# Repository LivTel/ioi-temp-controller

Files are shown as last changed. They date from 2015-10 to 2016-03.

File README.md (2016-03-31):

ioi-temp-controller
=============

# Overview

This package contains the electronic schematics and arduino code to drive a 
10 microamp excitation current required by the DT-400 series temperature 
sensor diodes inside IO:I's cryostat. This facility was originally provided 
by the Lakeshore 331 temperature controller. 

# Commands

The mac, ip, gateway and subnet addresses need to be configured first.

On upload to an ethernet arduino, a socket server is instantiated to serve a limited command set previously 
used by IO:I's ICS. The four commands that are currently available are:

| Command        | Description                        |
| :------------- | :----------------                  | 
| KRDG?A         | Read temperature from sensor A (K) |
| KRDG?B         | Read temperature from sensor B (K) |
| VRDG?A         | Read voltage from sensor A (V)     |
| VRDG?B         | Read voltage from sensor B (V)     |

The socket server is blocking, and must not be held open for prolonged periods by a single machine.

## Schematic

The schematic is as follows.

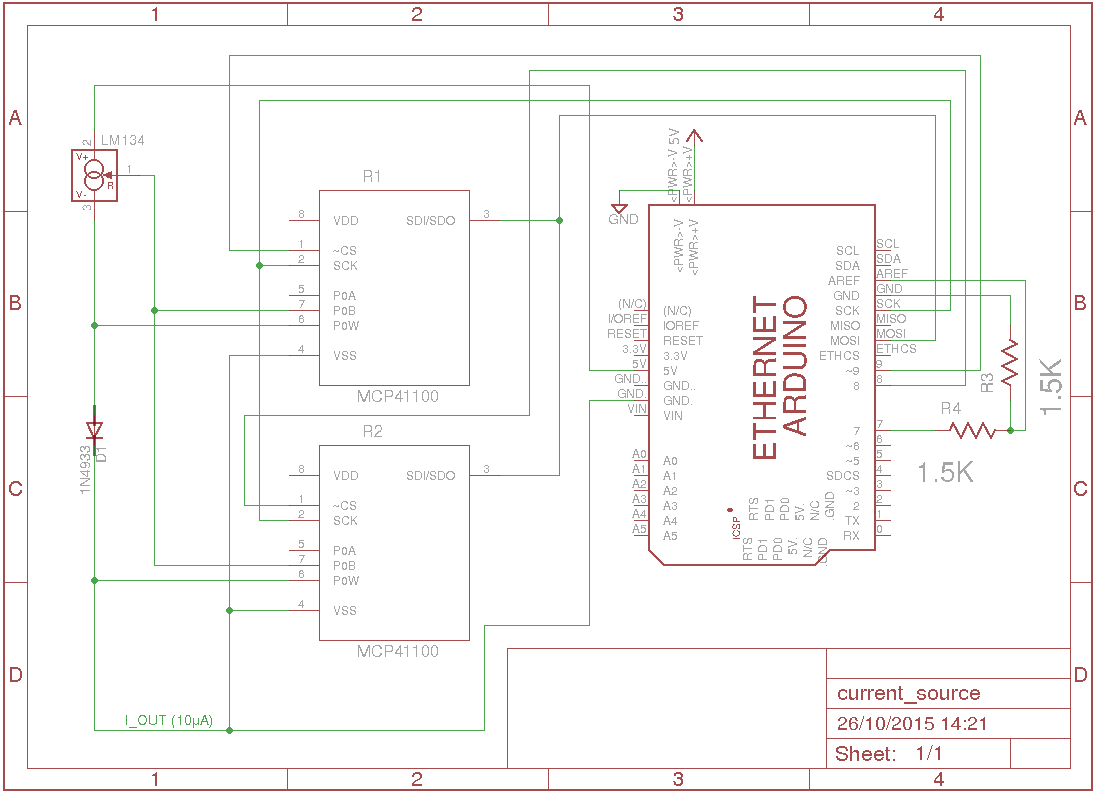
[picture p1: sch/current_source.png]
Schematic

 
The LM134 IC provides a temperature dependent current source. The magnitude of this 
current source is modulated by the two digital pots R1 & R2 (MCP41100). The 
temperature dependence is largely removed by diode D1 (1N4933). 

Note that the ETHCS pin is not used for clock selects!

# I/O Configuration

Definitions for I/O should not need to be changed if the wiring follows the schematic above *and* the 
temperature sensor wiring follows:

| Pin            | Description       |
| :------------- | :---------------- | 
| 2              | T2 V-             |
| 3              | T2 V+             |
| 4              | T1 V-             |
| 5              | T1 V+             |

# Current Magnitude and Temperature Calibration Coefficients

The set current [**SET\_CURRENT**] must be set so that it lies within the capability defined by the relative 
resistances of the digital pots. See p8 of the LM234 component manual in `man/` for a description of how the 
current magnitude is defined using the two pots.

The temperature sensor calibration is defined by the coefficients [**DIODE\_TEMPERATURE\_COEFFS**] and 
a corresponding reference voltage [**REFERENCE\_VOLTAGE**]. This has been set (as of 19/10/15) for 
a DT471 series diode.

# Known Issues

A 2.5V reference voltage is fed to the reference pin to increase the accuracy of the A2D conversion whilst still
remaining in range of the full output voltage of the diode at RT down to 80K. Currently, with the 10bit conversion 
and a diode temperature coefficient of -2.5mV/degC, the system is only accurate to [2.5/(2^10)]/(2.5*10^-3) 
degC == 1 degC. This could be improved by either i) addition of a more accurate A2D circuit, or ii) reducing the range 
over which the sensor can be read.

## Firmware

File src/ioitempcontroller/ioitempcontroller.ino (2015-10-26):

// LM134 datasheet (http://www.ti.com/lit/ds/symlink/lm234.pdf)
// MCP41100 datasheet (http://docs-europe.electrocomponents.com/webdocs/1380/0900766b81380ca2.pdf)
// DT471 datasheet (http://www.lakeshore.com/Documents/LSTC_DT400_l.pdf)

#include <SPI.h>
#include <Ethernet.h>

// NETWORK
// -------
// ARI LOCAL NETWORK
//byte mac[]     = { 0x90, 0xA2, 0xDA, 0x0E, 0x50, 0x9E };
//byte ip[]      = { 150, 204, 241, 253 }; 
//byte gateway[] = { 150, 204 ,241 ,254 };
//byte subnet[]  = { 255, 255 ,255 ,0 };

// TELESCOPE NETWORK
// ioitempcontroller
//byte mac[]     = { 0x90, 0xA2, 0xDA, 0x0E, 0x50, 0x9E };
byte mac[]     = { 0x90, 0xA2, 0xDA, 0x0D, 0xCB, 0x08 };
byte ip[]      = { 192, 168, 1, 75 };
byte gateway[] = { 192, 168 ,1 ,254 };
byte subnet[]  = { 255, 255 ,255 ,0 };

int SERVER_PORT = 8888;

// I/O
// ---
#define REF_pin 7                   // pin to pull high for voltage divided reference.
#define R1_CS_pin  9                // clock select for R1
#define R2_CS_pin  8                // clock select for R2
#define T1_ANALOG_PIN_VPLUS 5       // analog pin for T1 V+
#define T1_ANALOG_PIN_VMINUS 4      // analog pin for T1 V-
#define T2_ANALOG_PIN_VPLUS 3       // analog pin for T2 V+
#define T2_ANALOG_PIN_VMINUS 2      // analog pin for T2 V-

// CURRENT SOURCE
// --------------
// the following section works out what resistances are required to keep a particular set current
// n.b. you can't have a resistance value > the limit of the digital pots (~90K), this corresponds
// to a lower limit of ~13uA.
float SET_CURRENT             = 9*pow(10, -6);   // A
float DIODE_FORWARD_VOLTAGE   = 0.5;              // V
float DIODE_TEMPERATURE_COEFF = -2.5;             // mV/degC

// TEMPERATURE SENSOR
// ------------------
// AS OF 19/10/15, for DT471.
int DIODE_TEMPERATURE_ORDER = 5;
float DIODE_TEMPERATURE_COEFFS[6] = {-906.15255839, 3184.68704355, -4521.75268022, 3189.42006723, -1526.98411765, 668.57235871};
float REFERENCE_VOLTAGE = 2.427;

//float DIODE_FORWARD_VOLTAGE_TEMPERATURE_SENSOR   = 0.54294;  // V (DT471)
//float DIODE_TEMPERATURE_COEFF_TEMPERATURE_SENSOR = -2.0; // mV/degC (DT471)

// PROGRAM PARAMETERS
// --------------
#define NUMREADINGS     10      // number of readings to take to define average analog read
#define NUMREADINGSOMIT 10      // number of analog reads to take before taking actual reading


float get_R1_for_given_set_current(float i_set, float resistor_ratio) {
  return ((resistor_ratio*67.7*pow(10, -3)) + ((67.7*pow(10, -3)) + DIODE_FORWARD_VOLTAGE))/(resistor_ratio*i_set);  // this is taken from p9 of the lm134 datasheet
}

int digitalPotWrite(int value, int address, int pin)
{
  digitalWrite(pin, LOW);
  SPI.transfer(address);
  SPI.transfer(value);
  digitalWrite(pin, HIGH);
}

void BubbleSort(float analogValues[])
{  
  int i, j;
  for (i=0; i<NUMREADINGS; i++)
  {
    for (j=0; j<i; j++)
    {
      if (analogValues[i] > analogValues[j]) // out of order?
      {
        // swap
        float temp = analogValues[i];
        analogValues[i] = analogValues[j];
        analogValues[j] = temp;
      }
    }
  }
}

float readSensor(int sensor, boolean returnT)
{
  int pin_vplus;
  int pin_vminus;
  switch(sensor)
  {
    case 1:
      pin_vplus = T1_ANALOG_PIN_VPLUS;
      pin_vminus = T1_ANALOG_PIN_VMINUS;
      break;
    case 2:
      pin_vplus = T2_ANALOG_PIN_VPLUS;
      pin_vminus = T2_ANALOG_PIN_VMINUS;
      break;      
    default:
      return false;      
  } 
  for (int i=0; i<NUMREADINGSOMIT; i++)
  {      
    analogRead(pin_vplus);
    analogRead(pin_vminus);
  } 
  float sensor_readings[NUMREADINGS];
  float this_pin_vplus_voltage, this_pin_vminus_voltage;
  for (int i=0; i<NUMREADINGS; i++)
  {      
    this_pin_vplus_voltage = (analogRead(pin_vplus)/(pow(2, 10)))*REFERENCE_VOLTAGE; // 10 bit ADC
    this_pin_vminus_voltage = (analogRead(pin_vminus)/(pow(2, 10)))*REFERENCE_VOLTAGE; // 10 bit ADC
    sensor_readings[i] = this_pin_vplus_voltage-this_pin_vminus_voltage; 
  } 
  
  BubbleSort(sensor_readings);    
  float avV = NUMREADINGS % 2 ? sensor_readings[NUMREADINGS/2] : (sensor_readings[NUMREADINGS/2 - 1] + sensor_readings[NUMREADINGS/2])/2;    
  
  float avT = 0;
  for (int i=0; i<=DIODE_TEMPERATURE_ORDER; i++) 
  {
     avT += DIODE_TEMPERATURE_COEFFS[i]*pow(avV, DIODE_TEMPERATURE_ORDER-i) ;
  }
   
  if (returnT) 
  {
    return avT;
  } else {
    return avV;
  }
}

EthernetServer server(SERVER_PORT);

void setup()
{
  SPI.begin();
  Serial.begin(9600);
  Ethernet.begin(mac, ip, gateway, subnet); // start the ethernet connection
  server.begin();                           // and begin listening for TCP connections

  analogReference(EXTERNAL);  // 2.5V with 1.5k, 1.5k divider

  pinMode (R1_CS_pin, OUTPUT);
  pinMode (R2_CS_pin, OUTPUT);
  
  pinMode (REF_pin, OUTPUT);
  digitalWrite(REF_pin, HIGH);

  float resistor_ratio   = ((abs(DIODE_TEMPERATURE_COEFF)*pow(10, -3)) - (227*pow(10, -6)))/(227*pow(10, -6));   // this is taken from p8 of the lm134 datasheet, assuming -2mV/C for the temperature coeff of the diode
  float R1               = get_R1_for_given_set_current(SET_CURRENT, resistor_ratio);
  float R2               = resistor_ratio*R1;

  int R1_byte = ceil(R1/((90000.-100.)/255.));
  int R2_byte = ceil(R2/((90000.-100.)/255.));
  
  if (R1_byte > 254) {
    Serial.println("R1 is out of range. Setting to highest value."); 
    R1_byte = 254;
  } else if (R1_byte < 0) {
    Serial.println("R1 is out of range. Setting to lowest value."); 
    R1_byte = 0;
  }
  
  if (R2_byte > 254) {
    Serial.println("R2 is out of range. Setting to highest value."); 
    R2_byte = 254;
  } else if (R2_byte < 0) {
    Serial.println("R2 is out of range. Setting to lowest value."); 
    R2_byte = 0;
  }
  
  Serial.print("R1 = ");
  Serial.print(R1);
  Serial.print(" = ");
  Serial.println(R1_byte);
  Serial.print("R2 = ");;
  Serial.print(R2);
  Serial.print(" = ");
  Serial.println(R2_byte);
  
  digitalPotWrite(R1_byte, 0x11, R1_CS_pin);
  digitalPotWrite(R2_byte, 0x11, R2_CS_pin); 
}

void loop()
{
  EthernetClient client = server.available();
  if (client) {
    String clientMsg = "";
    while (client.connected()) {
      // transmit
      while (client.available()) {
        char c = client.read();
        clientMsg+=c;
        if (c == '\n') {
          if (clientMsg.indexOf("KRDG?A") >= 0) {
            float rtn = readSensor(1, true);
            client.println(rtn);
          } else if (clientMsg.indexOf("KRDG?B") >= 0) {
            float rtn = readSensor(2, true);
            client.println(rtn);
          } if (clientMsg.indexOf("VRDG?A") >= 0) {
            float rtn = readSensor(1, false);
            client.println(rtn);
          } else if (clientMsg.indexOf("VRDG?B") >= 0) {
            float rtn = readSensor(2, false);
            client.println(rtn);
          }
          clientMsg = "";
          client.flush();
        } 
      }
    }
  }  
}

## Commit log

2015-10-12 init commit
    [current_source.brd, current_source.sch]
2016-03-31 Updated README and images.
    [current_source.sch]
